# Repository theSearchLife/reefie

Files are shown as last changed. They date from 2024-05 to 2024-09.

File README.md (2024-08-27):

---
description: >-
  Data logging device for https://thesearch.life/the-coral-reef-philippines/
  project.
---

# Introduction

**Documentation view** - [https://thesearch-life.gitbook.io/reefie](https://thesearch-life.gitbook.io/reefie)

## Description

Battery powered device, encapsulated in watersealed enclosure to be able withstand 30m depths. It has sensory probes that capture and log data to SD card.

Data captured:

* Temperature
* Dissolved oxygen saturation
* Turbidity
* Conductivity
* Total dissolved solids
* Salinity
* Specific gravity
* Pressure

BOM -&#x20;

Hardware design done in FreeCAD 0.21.2 with Assembly4 workbench  for assembly. [https://github.com/theSearchLife/reefie/tree/main/hardware](https://github.com/theSearchLife/reefie/tree/main/hardware)

All files for 3D printing at [https://github.com/theSearchLife/reefie/tree/main/hardware/3D\_printing](https://github.com/theSearchLife/reefie/tree/main/hardware/3D\_printing) folder or can be exported from FreeCAD file.

Electronics wiring schematic in KiCAD 7.0 [https://github.com/theSearchLife/reefie/tree/main/hardware](https://github.com/theSearchLife/reefie/tree/main/hardware)

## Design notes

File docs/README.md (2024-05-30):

# Description

##

##

To pull CAD files install git LFS [https://git-lfs.com/](https://git-lfs.com/)

## BOM

### Custom cables

command for generating image from main dir

```
wireviz -f p -o docs/.gitbook/assets/ hardware/analog_harness.yaml
```

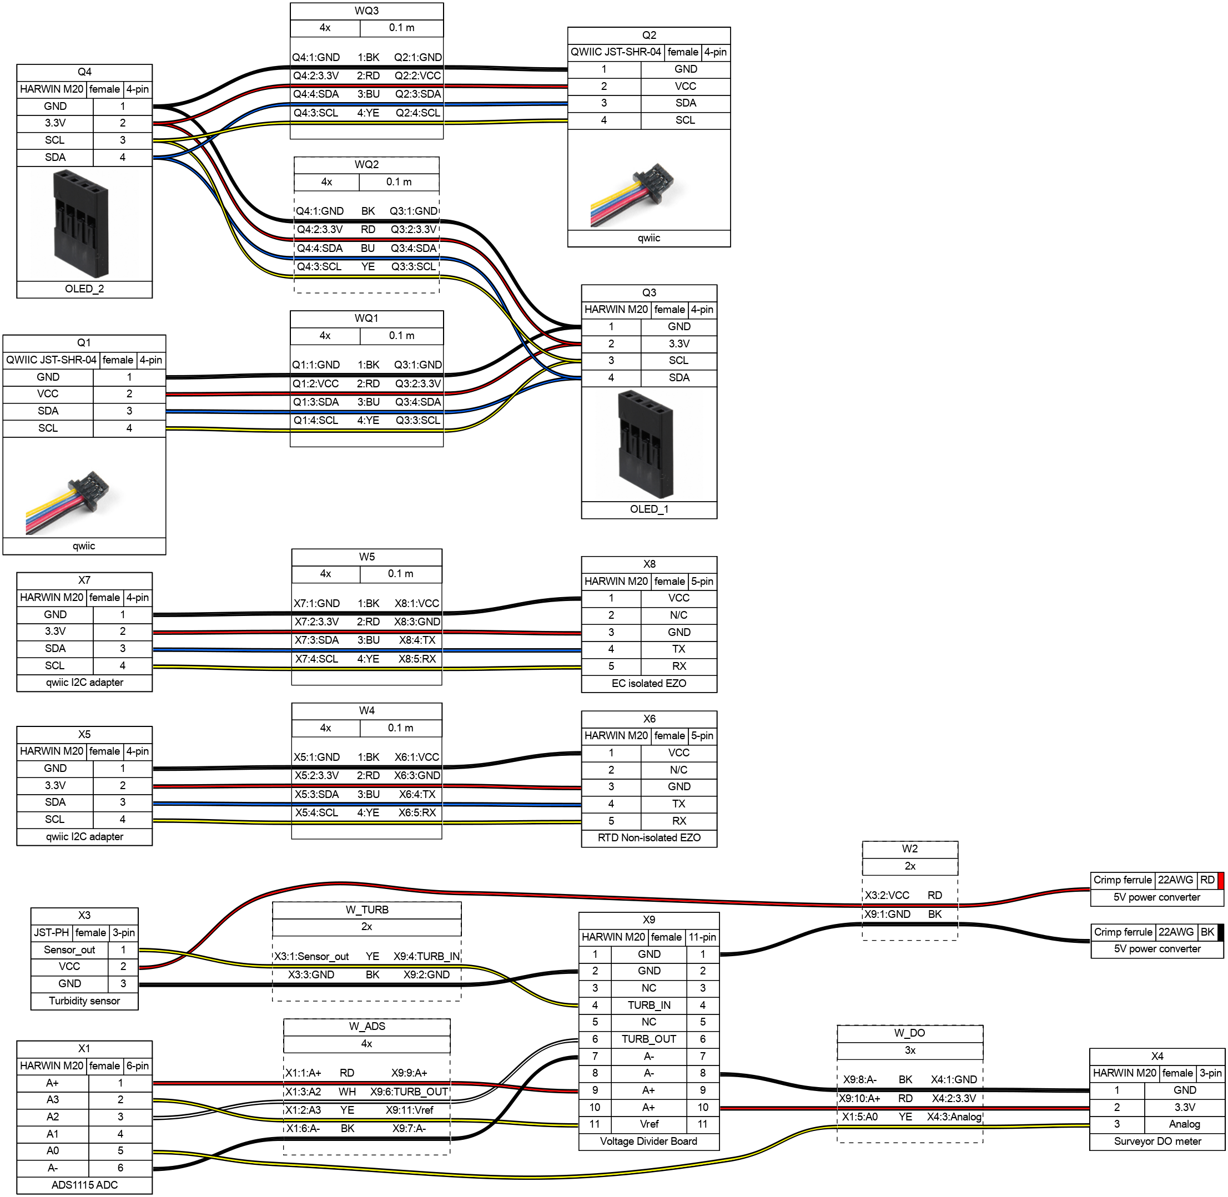
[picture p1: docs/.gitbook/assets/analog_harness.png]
<figure><figcaption></figcaption></figure>

## Firmware setup

VS Code

PlatformIO with dependencies

USB serial permissions

if USB device not found remove "apt remove brltty"

Depending on IDE need to manually configure to download mode\
\
Configure EZO probes to I2C mode

## Development notes

### I2C addresses

* 0x36 - MAX17048 - Fuel Gauge, Battery monitoring (on dev board)
* 0x48 - ADS1115 - ADC
* 0x49 - ADS1115 - (If A0/Addrees pin Soldered to HIGH) - ADC
* 0x64 - EZO-EC - Embedded Conductivity Circuit
* 0x66 - EZO-RTD Embedded Temperature Circuit
* 0x76 - MS5803-14BA - Pressure sensor

Can use Adafruit TestBed > I2CScan example to test/detect all I2C devices. [https://learn.adafruit.com/scanning-i2c-addresses/arduino-using-testbed](https://learn.adafruit.com/scanning-i2c-addresses/arduino-using-testbed)

## Useful links / References

<details>

<summary>SparkFun Thing Plus - ESP32 WROOM (USB-C)</summary>

* Sparkfun [https://www.sparkfun.com/products/20168](https://www.sparkfun.com/products/20168)
* Schematic [https://cdn.sparkfun.com/assets/5/9/7/4/1/SparkFun\_Thing\_Plus\_ESP32-WROOM\_C\_schematic2.pdf](https://cdn.sparkfun.com/assets/5/9/7/4/1/SparkFun\_Thing\_Plus\_ESP32-WROOM\_C\_schematic2.pdf)
* Graphical datasheet [https://cdn.sparkfun.com/assets/3/9/5/f/e/SparkFun\_Thing\_Plus\_ESP32\_WROOM\_C\_graphical\_datasheet2.pdf](https://cdn.sparkfun.com/assets/3/9/5/f/e/SparkFun\_Thing\_Plus\_ESP32\_WROOM\_C\_graphical\_datasheet2.pdf)
* GitHub Hardware repositore with firmware test for hardware features [https://github.com/sparkfun/SparkFun\_Thing\_Plus\_ESP32\_WROOM\_C](https://github.com/sparkfun/SparkFun\_Thing\_Plus\_ESP32\_WROOM\_C)

</details>

<details>

<summary>SparkFun Pressure Sensor Breakout - MS5803-14BA</summary>

* Sparkfun [https://www.sparkfun.com/products/12909](https://www.sparkfun.com/products/12909)
* Schematic - [https://cdn.sparkfun.com/datasheets/Sensors/Weather/MS5803-14BA\_Breakout\_v10.pdf](https://cdn.sparkfun.com/datasheets/Sensors/Weather/MS5803-14BA\_Breakout\_v10.pdf)
* Datasheet [https://cdn.sparkfun.com/datasheets/Sensors/Weather/ms5803\_14ba.pdf](https://cdn.sparkfun.com/datasheets/Sensors/Weather/ms5803\_14ba.pdf)

</details>

<details>

<summary>ADS115 Adafruit</summary>

* downloads [https://learn.adafruit.com/adafruit-4-channel-adc-breakouts/downloads](https://learn.adafruit.com/adafruit-4-channel-adc-breakouts/downloads)
* Pinouts [https://learn.adafruit.com/adafruit-4-channel-adc-breakouts/pinouts](https://learn.adafruit.com/adafruit-4-channel-adc-breakouts/pinouts)

</details>

<details>

<summary>Gravity: Analog Turbidity Sensor for Arduino</summary>

* DFRobot [https://www.dfrobot.com/product-1394.html](https://www.dfrobot.com/product-1394.html)
* DFRobot wiki [https://wiki.dfrobot.com/Turbidity\_sensor\_SKU\_\_SEN0189](https://wiki.dfrobot.com/Turbidity\_sensor\_SKU\_\_SEN0189)
* Sensor [https://dfimg.dfrobot.com/nobody/wiki/8e585d98aafe2bab22be39c5b68165c5.pdf](https://dfimg.dfrobot.com/nobody/wiki/8e585d98aafe2bab22be39c5b68165c5.pdf)
* Schematic [https://github.com/Arduinolibrary/DFRobot\_Turbidity\_sensor/blob/master/SEN0189%20Turbidity%20sensor%28V1.0%29%20schematic.pdf](https://github.com/Arduinolibrary/DFRobot\_Turbidity\_sensor/blob/master/SEN0189%20Turbidity%20sensor\(V1.0\)%20schematic.pdf)
* Probe [https://raw.githubusercontent.com/Arduinolibrary/DFRobot\_Turbidity\_sensor/master/Probe\_Dimension.png](https://raw.githubusercontent.com/Arduinolibrary/DFRobot\_Turbidity\_sensor/master/Probe\_Dimension.png)
* Adapter [https://raw.githubusercontent.com/Arduinolibrary/DFRobot\_Turbidity\_sensor/master/Adapter\_Dimension.png](https://raw.githubusercontent.com/Arduinolibrary/DFRobot\_Turbidity\_sensor/master/Adapter\_Dimension.png)

</details>

<details>

<summary>Gravity: Analog TDS Sensor/ Meter for Arduino</summary>

* DFRobot [https://www.dfrobot.com/product-1662.html](https://www.dfrobot.com/product-1662.html)
* DFRobot wiki [https://wiki.dfrobot.com/Gravity\_\_Analog\_TDS\_Sensor\_\_\_Meter\_For\_Arduino\_SKU\_\_SEN0244](https://wiki.dfrobot.com/Gravity\_\_Analog\_TDS\_Sensor\_\_\_Meter\_For\_Arduino\_SKU\_\_SEN0244)
* Schematic [https://raw.githubusercontent.com/Arduinolibrary/Gravity\_Analog\_TDS\_Sensor\_For\_Arduino/master/Analog%20TDS%20Sensor(V1.0)%20Schematic.pdf](https://raw.githubusercontent.com/Arduinolibrary/Gravity\_Analog\_TDS\_Sensor\_For\_Arduino/master/Analog%20TDS%20Sensor\(V1.0\)%20Schematic.pdf)
* Adapter layout [https://raw.githubusercontent.com/Arduinolibrary/Gravity\_Analog\_TDS\_Sensor\_For\_Arduino/master/Analog%20TDS%20Sensor(V1.0)%20Layout.pdf](https://raw.githubusercontent.com/Arduinolibrary/Gravity\_Analog\_TDS\_Sensor\_For\_Arduino/master/Analog%20TDS%20Sensor\(V1.0\)%20Layout.pdf)
* GitHub library [https://github.com/DFRobot/GravityTDS](https://github.com/DFRobot/GravityTDS)

</details>

<details>

<summary>PowerBoost 500 Basic - 5V USB Boost @ 500mA from 1.8V+</summary>

* Adafruit [https://www.adafruit.com/product/1903](https://www.adafruit.com/product/1903)
* Schematic [https://cdn-learn.adafruit.com/assets/assets/000/017/017/original/adafruit\_products\_tps61090.png?1401312193](https://cdn-learn.adafruit.com/assets/assets/000/017/017/original/adafruit\_products\_tps61090.png?1401312193)
* Datasheet [https://cdn-shop.adafruit.com/datasheets/tps61090.pdf](https://cdn-shop.adafruit.com/datasheets/tps61090.pdf)

</details>

<details>

<summary>Inline PT-1000 Temperature Kit</summary>

* AtlasScientific [https://atlas-scientific.com/kits/inline-temperature-kit/](https://atlas-scientific.com/kits/inline-temperature-kit/)
* EZO™ RTD Circuit Datasheet [https://files.atlas-scientific.com/EZO\_RTD\_Datasheet.pdf](https://files.atlas-scientific.com/EZO\_RTD\_Datasheet.pdf)
* PT-1000 Temperature Probe Datasheet [https://files.atlas-scientific.com/PT-1000-probe.pdf](https://files.atlas-scientific.com/PT-1000-probe.pdf)
* EZO™ Carrier Board Specsheet [https://files.atlas-scientific.com/EZO-carrier-board-non-isolated.pdf](https://files.atlas-scientific.com/EZO-carrier-board-non-isolated.pdf)
* Github I2C library [https://github.com/Atlas-Scientific/Ezo\_I2c\_lib](https://github.com/Atlas-Scientific/Ezo\_I2c\_lib)
* I2C Sample code [https://files.atlas-scientific.com/Ardunio-I2C-RTD-sample-code.pdf](https://files.atlas-scientific.com/Ardunio-I2C-RTD-sample-code.pdf)

</details>

<details>

<summary>Mini Conductivity K 1.0 Kit</summary>

* AtlasScientific [https://atlas-scientific.com/kits/mini-conductivity-k-1-0-kit/](https://atlas-scientific.com/kits/mini-conductivity-k-1-0-kit/)
* EZO™ Conductivity Circuit Datasheet [https://files.atlas-scientific.com/EC\_EZO\_Datasheet.pdf](https://files.atlas-scientific.com/EC\_EZO\_Datasheet.pdf)
* Mini Conductivity Probe K 1.0 Datasheet [https://files.atlas-scientific.com/Mini\_EC\_K\_1.0\_probe.pdf](https://files.atlas-scientific.com/Mini\_EC\_K\_1.0\_probe.pdf)
* Electrically Isolated EZO™ Carrier Board Datasheet [https://files.atlas-scientific.com/electrically-isolated-ezo-carrier-board.pdf](https://files.atlas-scientific.com/electrically-isolated-ezo-carrier-board.pdf)
* EZO™ Conductivity Accuracy Graph [https://files.atlas-scientific.com/conductivity\_accuracy\_graph.pdf](https://files.atlas-scientific.com/conductivity\_accuracy\_graph.pdf)
* Wiring Diagram [https://files.atlas-scientific.com/ezo-ec-wiringdiagram.pdf](https://files.atlas-scientific.com/ezo-ec-wiringdiagram.pdf)
* How to properly cut your probe cable [https://files.atlas-scientific.com/how-to-properly-cut-probe-cables.pdf](https://files.atlas-scientific.com/how-to-properly-cut-probe-cables.pdf)
* I2C sample code [https://files.atlas-scientific.com/Ardunio-I2C-EC-sample-code.pdf](https://files.atlas-scientific.com/Ardunio-I2C-EC-sample-code.pdf)
* EZO I2C Library [https://github.com/Atlas-Scientific/Ezo\_I2c\_lib](https://github.com/Atlas-Scientific/Ezo\_I2c\_lib)
* I2C mode selection [https://www.instructables.com/UART-AND-I2C-MODE-SWITCHING-FOR-ATLAS-SCIENTIFIC-E/](https://www.instructables.com/UART-AND-I2C-MODE-SWITCHING-FOR-ATLAS-SCIENTIFIC-E/)

</details>

<details>

<summary>Surveyor™ Analog Dissolved Oxygen Kit</summary>

* AtlasScientific [https://atlas-scientific.com/kits/surveyor-analog-do-kit/](https://atlas-scientific.com/kits/surveyor-analog-do-kit/)
* Surveyor™ Analog D.O. Meter Datasheet [https://files.atlas-scientific.com/Surveyor-DO-datasheet.pdf](https://files.atlas-scientific.com/Surveyor-DO-datasheet.pdf)
* Mini Lab Grade Dissolved Oxygen Probe Datasheet [https://files.atlas-scientific.com/Mini\_DO\_probe.pdf](https://files.atlas-scientific.com/Mini\_DO\_probe.pdf)
* Dissolved Oxygen | Common Mistakes | Air Bubble [https://youtu.be/1I1Sk9pt47c](https://youtu.be/1I1Sk9pt47c)
* Dissolved Oxygen | Common Mistakes | Stagnant vs Moving Water [https://youtu.be/d9zkxkv55SE](https://youtu.be/d9zkxkv55SE)
* Dissolved Oxygen | Common Mistakes | Damaged Membrane [https://youtu.be/PiXnvrTnVjs](https://youtu.be/PiXnvrTnVjs)
* Dissolved Oxygen Calculator [https://atlas-scientific.com/dissolved-oxygen-calculator](https://atlas-scientific.com/dissolved-oxygen-calculator)
* Arduino Sample Code [https://files.atlas-scientific.com/surveyor-DO-ardunio-code.pdf](https://files.atlas-scientific.com/surveyor-DO-ardunio-code.pdf)

</details>

<details>

<summary>Surveyor™ Analog pH Kit</summary>

* AtlastScientific [https://atlas-scientific.com/kits/surveyor-analog-ph-kit/](https://atlas-scientific.com/kits/surveyor-analog-ph-kit/)
* Surveyor™ Analog pH Sensor / Meter Datasheet [https://files.atlas-scientific.com/Surveyor-pH-datasheet.pdf](https://files.atlas-scientific.com/Surveyor-pH-datasheet.pdf)
* Consumer Grade pH Probe Datasheet [https://files.atlas-scientific.com/consumer-grade-pH-probe.pdf](https://files.atlas-scientific.com/consumer-grade-pH-probe.pdf)
* pH Temperature Compensation Calculator [https://atlas-scientific.com/ph-temperature-calculator/](https://atlas-scientific.com/ph-temperature-calculator/)
* Arduino Sample Code [https://files.atlas-scientific.com/surveyor-pH-ardunio-code.pdf](https://files.atlas-scientific.com/surveyor-pH-ardunio-code.pdf)
*

</details>

<details>

<summary>Surveyor™ Analog Isolator</summary>

* AtlasScientific [https://atlas-scientific.com/carrier-boards/surveyor-analog-isolator/](https://atlas-scientific.com/carrier-boards/surveyor-analog-isolator/)
* Surveyor™ Analog Isolator Datasheet [https://files.atlas-scientific.com/Surveyor\_analog\_isolator\_datasheet.pdf](https://files.atlas-scientific.com/Surveyor\_analog\_isolator\_datasheet.pdf)
* Arduino Sample Code [https://files.atlas-scientific.com/atlas\_surveyor.zip](https://files.atlas-scientific.com/atlas\_surveyor.zip)
* Surveyor™ Analog Isolator 3D model (\*step) [https://files.atlas-scientific.com/ISO-Gravity.zip](https://files.atlas-scientific.com/ISO-Gravity.zip)

</details>

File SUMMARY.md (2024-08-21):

# Table of contents

* [Introduction](README.md)
* [Assembly instructions](assembly-instructions/README.md)
  * [Sensors](assembly-instructions/page-1.md)
  * [Hardware](assembly-instructions/page-1-1.md)
  * [Electronics wiring](assembly-instructions/page-1-2.md)
  * [Inside Electronics](assembly-instructions/page-1-3.md)
  * [External assembly](assembly-instructions/external-assembly.md)
  * [Firmware setup](assembly-instructions/firmware-setup.md)
* [Usage / Maintenance](usage-maintenance.md)
* [Useful links / Datasheets / References](useful-links-datasheets-references.md)

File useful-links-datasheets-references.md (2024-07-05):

# Useful links / Datasheets / References

<details>

<summary>SparkFun Thing Plus - ESP32 WROOM (USB-C)</summary>

* Sparkfun [https://www.sparkfun.com/products/20168](https://www.sparkfun.com/products/20168)
* Schematic [https://cdn.sparkfun.com/assets/5/9/7/4/1/SparkFun\_Thing\_Plus\_ESP32-WROOM\_C\_schematic2.pdf](https://cdn.sparkfun.com/assets/5/9/7/4/1/SparkFun\_Thing\_Plus\_ESP32-WROOM\_C\_schematic2.pdf)
* Graphical datasheet [https://cdn.sparkfun.com/assets/3/9/5/f/e/SparkFun\_Thing\_Plus\_ESP32\_WROOM\_C\_graphical\_datasheet2.pdf](https://cdn.sparkfun.com/assets/3/9/5/f/e/SparkFun\_Thing\_Plus\_ESP32\_WROOM\_C\_graphical\_datasheet2.pdf)
* GitHub Hardware repositore with firmware test for hardware features [https://github.com/sparkfun/SparkFun\_Thing\_Plus\_ESP32\_WROOM\_C](https://github.com/sparkfun/SparkFun\_Thing\_Plus\_ESP32\_WROOM\_C)
* Fuel Gauge MAX17048 [https://cdn.sparkfun.com/assets/b/b/2/c/b/MAX17048.pdf](https://cdn.sparkfun.com/assets/b/b/2/c/b/MAX17048.pdf)

</details>

<details>

<summary>SparkFun Pressure Sensor Breakout - MS5803-14BA</summary>

* Sparkfun [https://www.sparkfun.com/products/12909](https://www.sparkfun.com/products/12909)
* Schematic - [https://cdn.sparkfun.com/datasheets/Sensors/Weather/MS5803-14BA\_Breakout\_v10.pdf](https://cdn.sparkfun.com/datasheets/Sensors/Weather/MS5803-14BA\_Breakout\_v10.pdf)
* Datasheet [https://cdn.sparkfun.com/datasheets/Sensors/Weather/ms5803\_14ba.pdf](https://cdn.sparkfun.com/datasheets/Sensors/Weather/ms5803\_14ba.pdf)

</details>

<details>

<summary>ADS115 Adafruit</summary>

* downloads [https://learn.adafruit.com/adafruit-4-channel-adc-breakouts/downloads](https://learn.adafruit.com/adafruit-4-channel-adc-breakouts/downloads)
* Pinouts [https://learn.adafruit.com/adafruit-4-channel-adc-breakouts/pinouts](https://learn.adafruit.com/adafruit-4-channel-adc-breakouts/pinouts)

</details>

<details>

<summary>RTC DS3231 Adafruit</summary>

* Adafruit [https://www.adafruit.com/product/5188](https://www.adafruit.com/product/5188)
* Adafruit Learning [https://learn.adafruit.com/adafruit-ds3231-precision-rtc-breakout/](https://learn.adafruit.com/adafruit-ds3231-precision-rtc-breakout/)
* Datasheet [https://www.analog.com/media/en/technical-documentation/data-sheets/DS3231.pdf](https://www.analog.com/media/en/technical-documentation/data-sheets/DS3231.pdf)
* Digikey [https://www.digikey.it/it/products/detail/adafruit-industries-llc/5188/15189155](https://www.digikey.it/it/products/detail/adafruit-industries-llc/5188/15189155)

</details>

<details>

<summary>Gravity: Analog Turbidity Sensor for Arduino</summary>

* DFRobot [https://www.dfrobot.com/product-1394.html](https://www.dfrobot.com/product-1394.html)
* DFRobot wiki [https://wiki.dfrobot.com/Turbidity\_sensor\_SKU\_\_SEN0189](https://wiki.dfrobot.com/Turbidity\_sensor\_SKU\_\_SEN0189)
* Sensor [https://dfimg.dfrobot.com/nobody/wiki/8e585d98aafe2bab22be39c5b68165c5.pdf](https://dfimg.dfrobot.com/nobody/wiki/8e585d98aafe2bab22be39c5b68165c5.pdf)
* Schematic [https://github.com/Arduinolibrary/DFRobot\_Turbidity\_sensor/blob/master/SEN0189%20Turbidity%20sensor%28V1.0%29%20schematic.pdf](https://github.com/Arduinolibrary/DFRobot\_Turbidity\_sensor/blob/master/SEN0189%20Turbidity%20sensor\(V1.0\)%20schematic.pdf)
* Probe [https://raw.githubusercontent.com/Arduinolibrary/DFRobot\_Turbidity\_sensor/master/Probe\_Dimension.png](https://raw.githubusercontent.com/Arduinolibrary/DFRobot\_Turbidity\_sensor/master/Probe\_Dimension.png)
* Adapter [https://raw.githubusercontent.com/Arduinolibrary/DFRobot\_Turbidity\_sensor/master/Adapter\_Dimension.png](https://raw.githubusercontent.com/Arduinolibrary/DFRobot\_Turbidity\_sensor/master/Adapter\_Dimension.png)

</details>

<details>

<summary>Gravity: Analog TDS Sensor/ Meter for Arduino</summary>

* DFRobot [https://www.dfrobot.com/product-1662.html](https://www.dfrobot.com/product-1662.html)
* DFRobot wiki [https://wiki.dfrobot.com/Gravity\_\_Analog\_TDS\_Sensor\_\_\_Meter\_For\_Arduino\_SKU\_\_SEN0244](https://wiki.dfrobot.com/Gravity\_\_Analog\_TDS\_Sensor\_\_\_Meter\_For\_Arduino\_SKU\_\_SEN0244)
* Schematic [https://raw.githubusercontent.com/Arduinolibrary/Gravity\_Analog\_TDS\_Sensor\_For\_Arduino/master/Analog%20TDS%20Sensor(V1.0)%20Schematic.pdf](https://raw.githubusercontent.com/Arduinolibrary/Gravity\_Analog\_TDS\_Sensor\_For\_Arduino/master/Analog%20TDS%20Sensor\(V1.0\)%20Schematic.pdf)
* Adapter layout [https://raw.githubusercontent.com/Arduinolibrary/Gravity\_Analog\_TDS\_Sensor\_For\_Arduino/master/Analog%20TDS%20Sensor(V1.0)%20Layout.pdf](https://raw.githubusercontent.com/Arduinolibrary/Gravity\_Analog\_TDS\_Sensor\_For\_Arduino/master/Analog%20TDS%20Sensor\(V1.0\)%20Layout.pdf)
* GitHub library [https://github.com/DFRobot/GravityTDS](https://github.com/DFRobot/GravityTDS)

</details>

<details>

<summary>PowerBoost 500 Basic - 5V USB Boost @ 500mA from 1.8V+</summary>

* Adafruit [https://www.adafruit.com/product/1903](https://www.adafruit.com/product/1903)
* Schematic [https://cdn-learn.adafruit.com/assets/assets/000/017/017/original/adafruit\_products\_tps61090.png?1401312193](https://cdn-learn.adafruit.com/assets/assets/000/017/017/original/adafruit\_products\_tps61090.png?1401312193)
* Datasheet [https://cdn-shop.adafruit.com/datasheets/tps61090.pdf](https://cdn-shop.adafruit.com/datasheets/tps61090.pdf)

</details>

<details>

<summary>Inline PT-1000 Temperature Kit</summary>

* AtlasScientific [https://atlas-scientific.com/kits/inline-temperature-kit/](https://atlas-scientific.com/kits/inline-temperature-kit/)
* EZO™ RTD Circuit Datasheet [https://files.atlas-scientific.com/EZO\_RTD\_Datasheet.pdf](https://files.atlas-scientific.com/EZO\_RTD\_Datasheet.pdf)
* PT-1000 Temperature Probe Datasheet [https://files.atlas-scientific.com/PT-1000-probe.pdf](https://files.atlas-scientific.com/PT-1000-probe.pdf)
* EZO™ Carrier Board Specsheet [https://files.atlas-scientific.com/EZO-carrier-board-non-isolated.pdf](https://files.atlas-scientific.com/EZO-carrier-board-non-isolated.pdf)
* Github I2C library [https://github.com/Atlas-Scientific/Ezo\_I2c\_lib](https://github.com/Atlas-Scientific/Ezo\_I2c\_lib)
* I2C Sample code [https://files.atlas-scientific.com/Ardunio-I2C-RTD-sample-code.pdf](https://files.atlas-scientific.com/Ardunio-I2C-RTD-sample-code.pdf)

</details>

<details>

<summary>Mini Conductivity K 1.0 Kit</summary>

* AtlasScientific [https://atlas-scientific.com/kits/mini-conductivity-k-1-0-kit/](https://atlas-scientific.com/kits/mini-conductivity-k-1-0-kit/)
* EZO™ Conductivity Circuit Datasheet [https://files.atlas-scientific.com/EC\_EZO\_Datasheet.pdf](https://files.atlas-scientific.com/EC\_EZO\_Datasheet.pdf)
* Mini Conductivity Probe K 1.0 Datasheet [https://files.atlas-scientific.com/Mini\_EC\_K\_1.0\_probe.pdf](https://files.atlas-scientific.com/Mini\_EC\_K\_1.0\_probe.pdf)
* Electrically Isolated EZO™ Carrier Board Datasheet [https://files.atlas-scientific.com/electrically-isolated-ezo-carrier-board.pdf](https://files.atlas-scientific.com/electrically-isolated-ezo-carrier-board.pdf)
* EZO™ Conductivity Accuracy Graph [https://files.atlas-scientific.com/conductivity\_accuracy\_graph.pdf](https://files.atlas-scientific.com/conductivity\_accuracy\_graph.pdf)
* Wiring Diagram [https://files.atlas-scientific.com/ezo-ec-wiringdiagram.pdf](https://files.atlas-scientific.com/ezo-ec-wiringdiagram.pdf)
* How to properly cut your probe cable [https://files.atlas-scientific.com/how-to-properly-cut-probe-cables.pdf](https://files.atlas-scientific.com/how-to-properly-cut-probe-cables.pdf)
* I2C sample code [https://files.atlas-scientific.com/Ardunio-I2C-EC-sample-code.pdf](https://files.atlas-scientific.com/Ardunio-I2C-EC-sample-code.pdf)
* EZO I2C Library [https://github.com/Atlas-Scientific/Ezo\_I2c\_lib](https://github.com/Atlas-Scientific/Ezo\_I2c\_lib)
* I2C mode selection [https://www.instructables.com/UART-AND-I2C-MODE-SWITCHING-FOR-ATLAS-SCIENTIFIC-E/](https://www.instructables.com/UART-AND-I2C-MODE-SWITCHING-FOR-ATLAS-SCIENTIFIC-E/)

</details>

<details>

<summary>Surveyor™ Analog Dissolved Oxygen Kit</summary>

* AtlasScientific [https://atlas-scientific.com/kits/surveyor-analog-do-kit/](https://atlas-scientific.com/kits/surveyor-analog-do-kit/)
* Surveyor™ Analog D.O. Meter Datasheet [https://files.atlas-scientific.com/Surveyor-DO-datasheet.pdf](https://files.atlas-scientific.com/Surveyor-DO-datasheet.pdf)
* Mini Lab Grade Dissolved Oxygen Probe Datasheet [https://files.atlas-scientific.com/Mini\_DO\_probe.pdf](https://files.atlas-scientific.com/Mini\_DO\_probe.pdf)
* Dissolved Oxygen | Common Mistakes | Air Bubble [https://youtu.be/1I1Sk9pt47c](https://youtu.be/1I1Sk9pt47c)
* Dissolved Oxygen | Common Mistakes | Stagnant vs Moving Water [https://youtu.be/d9zkxkv55SE](https://youtu.be/d9zkxkv55SE)
* Dissolved Oxygen | Common Mistakes | Damaged Membrane [https://youtu.be/PiXnvrTnVjs](https://youtu.be/PiXnvrTnVjs)
* Dissolved Oxygen Calculator [https://atlas-scientific.com/dissolved-oxygen-calculator](https://atlas-scientific.com/dissolved-oxygen-calculator)
* Arduino Sample Code [https://files.atlas-scientific.com/surveyor-DO-ardunio-code.pdf](https://files.atlas-scientific.com/surveyor-DO-ardunio-code.pdf)

</details>

<details>

<summary>Surveyor™ Analog pH Kit</summary>

* AtlastScientific [https://atlas-scientific.com/kits/surveyor-analog-ph-kit/](https://atlas-scientific.com/kits/surveyor-analog-ph-kit/)
* Surveyor™ Analog pH Sensor / Meter Datasheet [https://files.atlas-scientific.com/Surveyor-pH-datasheet.pdf](https://files.atlas-scientific.com/Surveyor-pH-datasheet.pdf)
* Consumer Grade pH Probe Datasheet [https://files.atlas-scientific.com/consumer-grade-pH-probe.pdf](https://files.atlas-scientific.com/consumer-grade-pH-probe.pdf)
* pH Temperature Compensation Calculator [https://atlas-scientific.com/ph-temperature-calculator/](https://atlas-scientific.com/ph-temperature-calculator/)
* Arduino Sample Code [https://files.atlas-scientific.com/surveyor-pH-ardunio-code.pdf](https://files.atlas-scientific.com/surveyor-pH-ardunio-code.pdf)
*

</details>

<details>

<summary>Surveyor™ Analog Isolator</summary>

* AtlasScientific [https://atlas-scientific.com/carrier-boards/surveyor-analog-isolator/](https://atlas-scientific.com/carrier-boards/surveyor-analog-isolator/)
* Surveyor™ Analog Isolator Datasheet [https://files.atlas-scientific.com/Surveyor\_analog\_isolator\_datasheet.pdf](https://files.atlas-scientific.com/Surveyor\_analog\_isolator\_datasheet.pdf)
* Arduino Sample Code [https://files.atlas-scientific.com/atlas\_surveyor.zip](https://files.atlas-scientific.com/atlas\_surveyor.zip)
* Surveyor™ Analog Isolator 3D model (\*step) [https://files.atlas-scientific.com/ISO-Gravity.zip](https://files.atlas-scientific.com/ISO-Gravity.zip)

</details>

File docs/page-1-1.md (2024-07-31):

---
description: Preparation of sensors
---

# Sensors

## Pressure

<details>

<summary>MS583730BA01-50</summary>

**Components**

* Sensor [https://www.digikey.it/en/products/detail/te-connectivity-measurement-specialties/MS583730BA01-50/5629501?s=N4IgTCBcDaILIGUCsAOAzAdjQBgEIEFsBGAWiWxAF0BfIA](https://www.digikey.it/en/products/detail/te-connectivity-measurement-specialties/MS583730BA01-50/5629501?s=N4IgTCBcDaILIGUCsAOAzAdjQBgEIEFsBGAWiWxAF0BfIA)
* 3D printed
  * MS583730BA01-50-Enclosure\_inner
  * MS583730BA01-50- Enclosure\_outer
* Cable&#x20;
* SMD 0.1uF Capacitor
* o-ring
* Flexible Urethane 8800
  * Syringe to inject liquid inside casing

**Steps**

*   3D print

    * 6 Layer walls
    * 100% infill
    * PETG

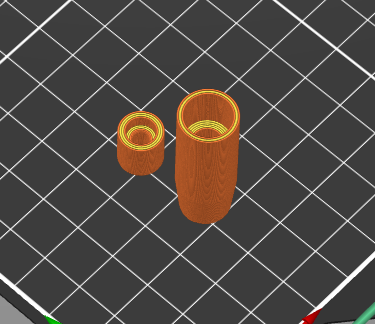
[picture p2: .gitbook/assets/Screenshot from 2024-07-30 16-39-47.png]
    

<!---->

* Solder capacitor and cable

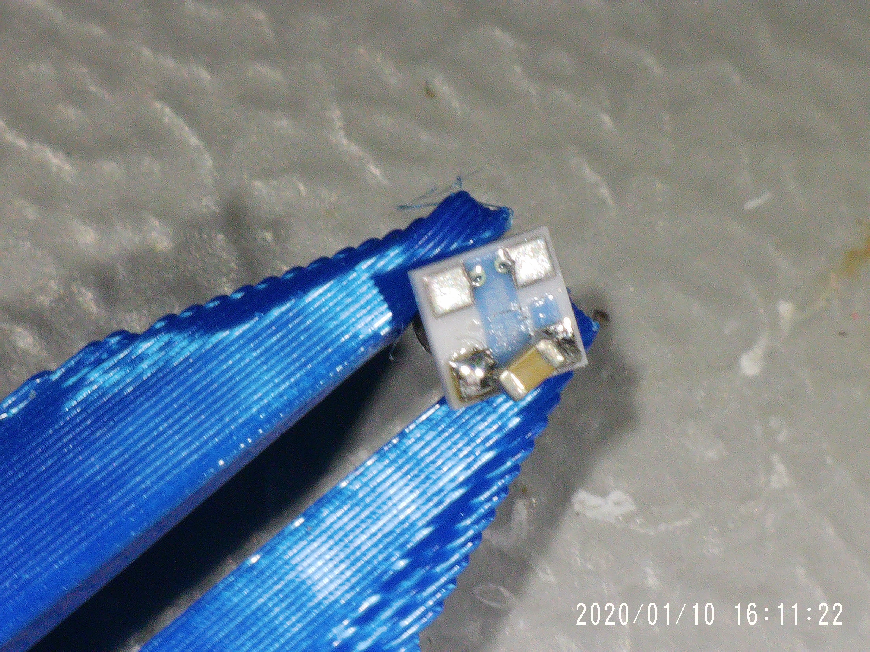
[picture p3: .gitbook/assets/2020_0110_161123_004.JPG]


* Apply conformal coating on soldering
* Install o-ring to sensor
* Clean cable with IPA
* Insert sensor to casing

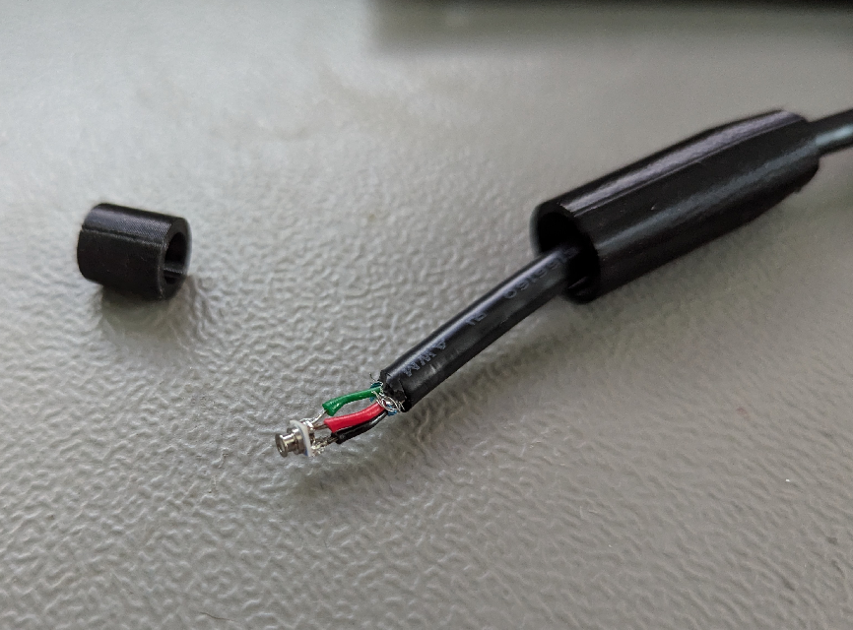
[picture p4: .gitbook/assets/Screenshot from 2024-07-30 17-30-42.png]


* Mount external casing

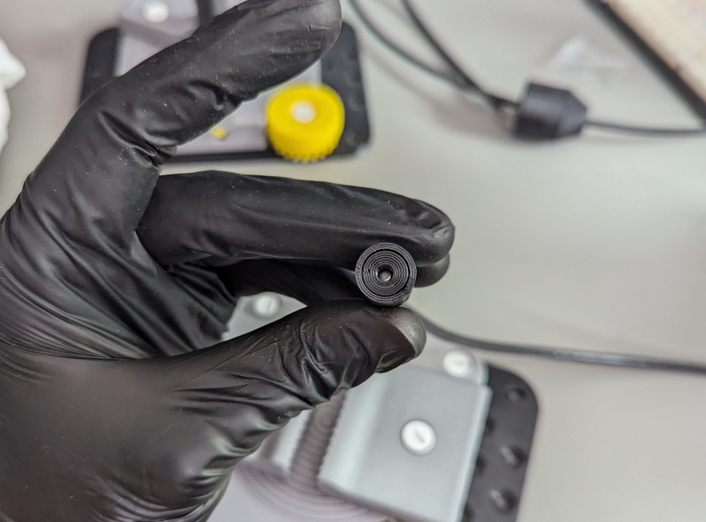
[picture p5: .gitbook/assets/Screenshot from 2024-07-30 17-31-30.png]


* Apply tape on the end to prevent leaking

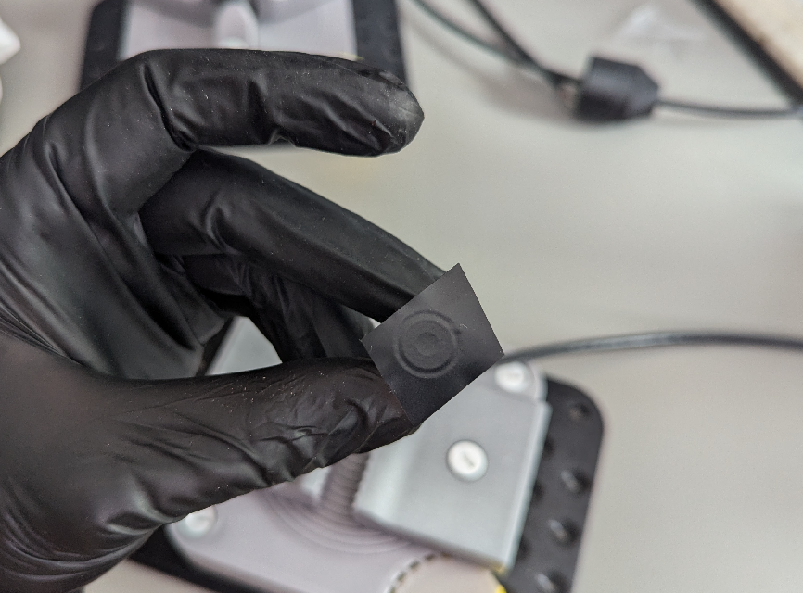
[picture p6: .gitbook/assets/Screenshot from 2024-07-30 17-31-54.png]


* Fill casing with Urethane (using syringe)

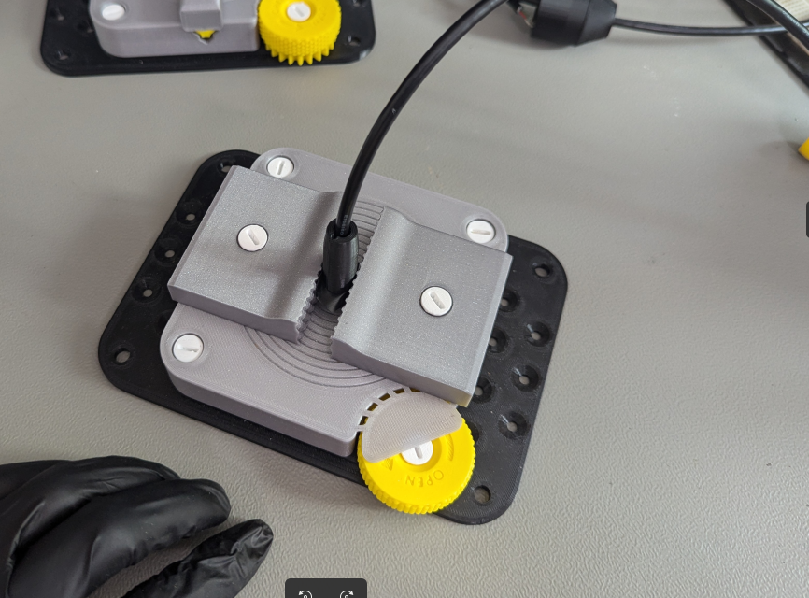
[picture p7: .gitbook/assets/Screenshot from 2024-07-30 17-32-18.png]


* Cure it

</details>

<details>

<summary>MS580314BA01-00</summary>

**Components**

* Sensor
* 3D printed
  * MS580314BA01-00-Enclosure\_inner
  * MS580314BA01-00 - Enclosure\_outer
* Cable
* Flexible Urethane 8800

**Steps**

* 3D print
  * 6 Layer walls
  * 100% infill
  * PETG

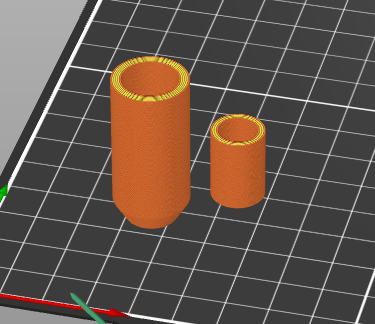
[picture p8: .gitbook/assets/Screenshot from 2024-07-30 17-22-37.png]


* Solder capacitor and cable
* Apply conformal coating
* Clean cable with IPA
* Insert sensor to casing

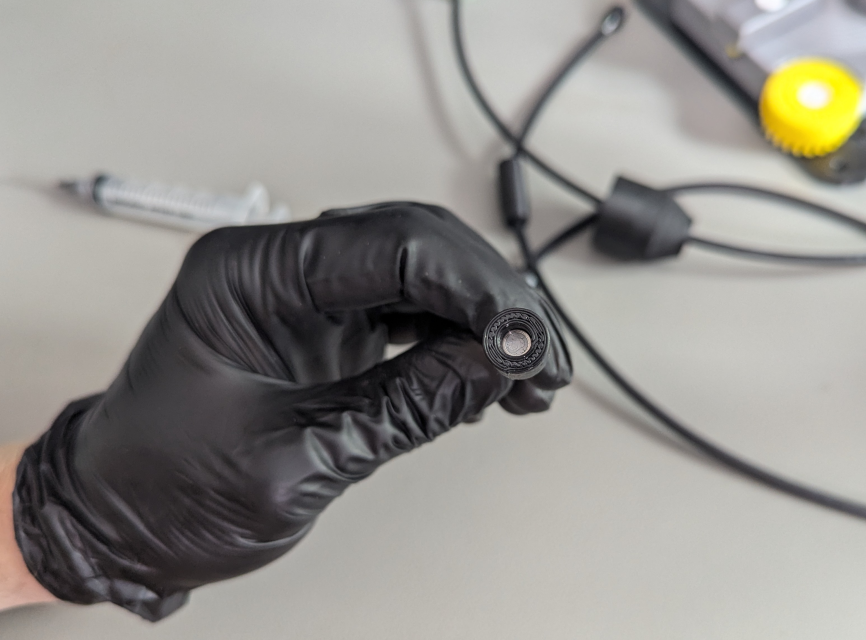
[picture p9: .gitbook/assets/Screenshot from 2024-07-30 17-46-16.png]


* Mount external casing
* Apply tape to prevent Urethane leaking

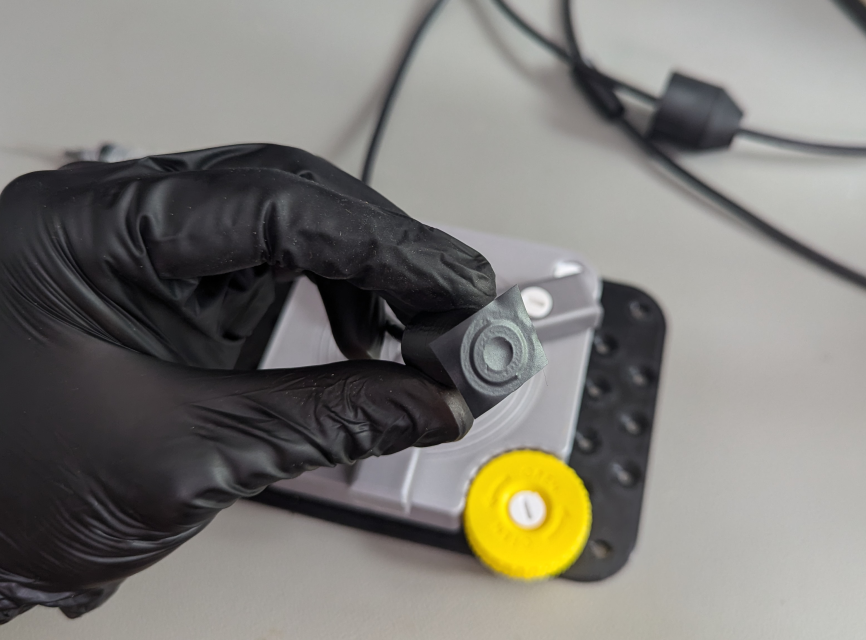
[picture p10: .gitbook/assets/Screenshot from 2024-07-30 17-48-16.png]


* Fill casing with Urethane
* Cure itdone

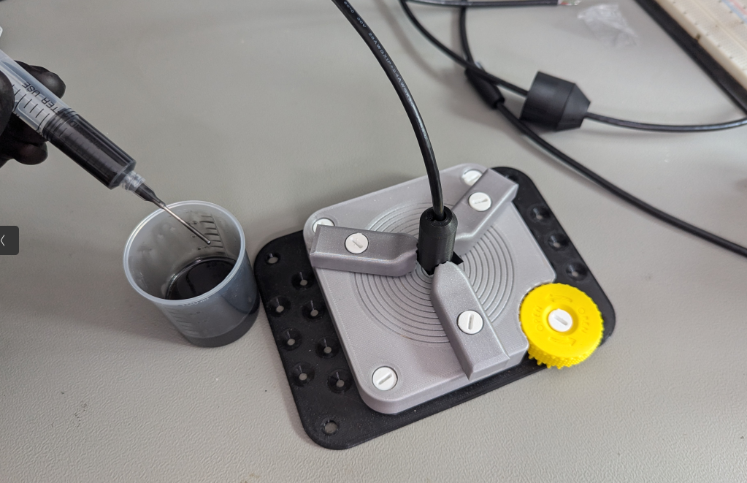
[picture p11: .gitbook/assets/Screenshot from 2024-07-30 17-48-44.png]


</details>

## Turbidity sensor

* Sensor [https://www.dfrobot.com/product-1394.html](https://www.dfrobot.com/product-1394.html)
* 3D print Casing
  * Turbidity\_Cover
  * 6 Layer wall
  * 100% infill
  * 10mm Brim width
  * PETG

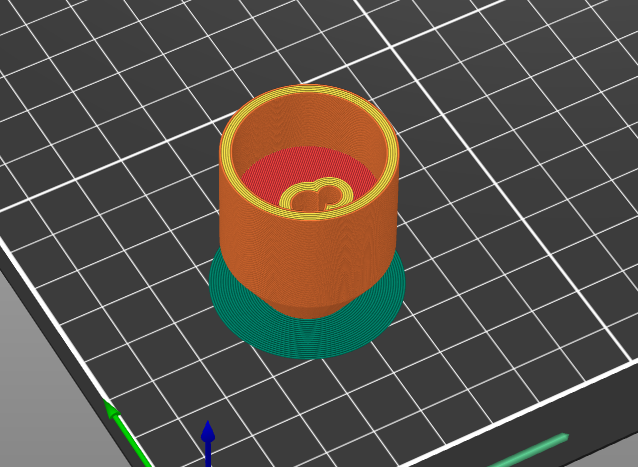
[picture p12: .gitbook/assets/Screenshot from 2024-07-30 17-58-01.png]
<figure><figcaption></figcaption></figure>

* Desolder JST connector

<div>

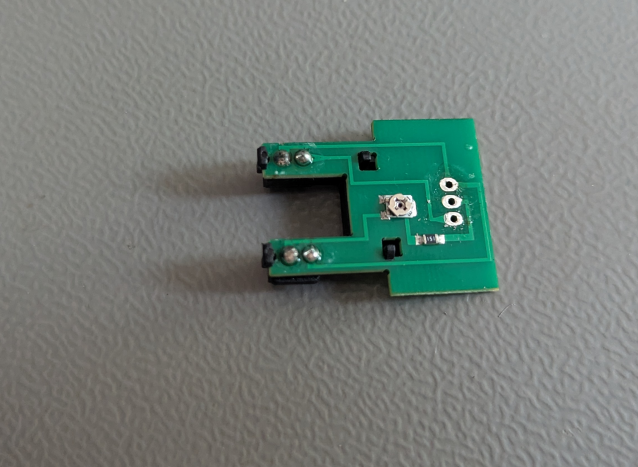
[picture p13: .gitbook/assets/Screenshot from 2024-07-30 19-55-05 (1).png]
<figure><figcaption></figcaption></figure>

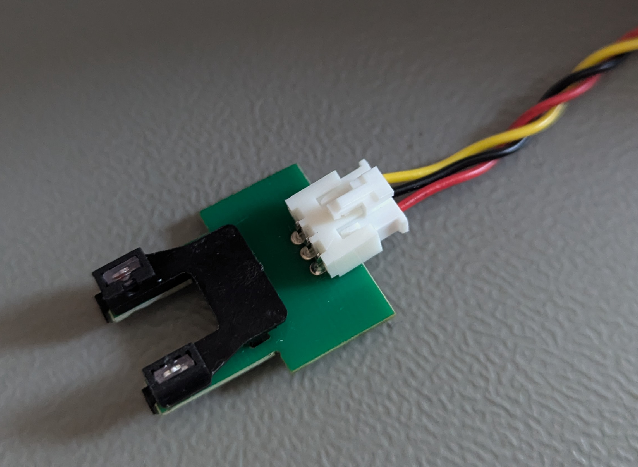
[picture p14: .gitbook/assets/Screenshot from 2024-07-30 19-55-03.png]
<figure><figcaption></figcaption></figure>

</div>

* Solder the cable
  * Red - VCC
  * Black - GND
  * Green - Signal

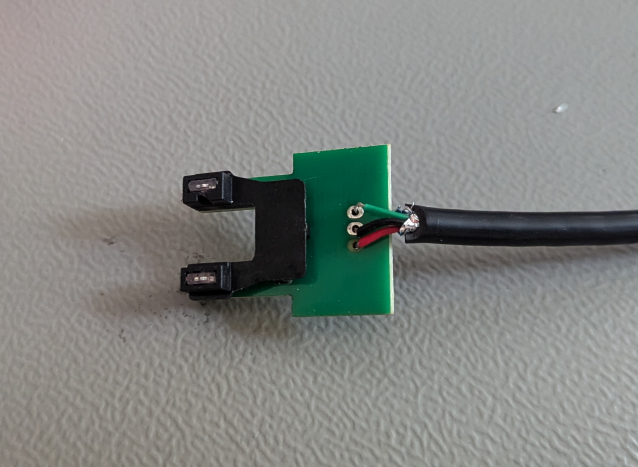
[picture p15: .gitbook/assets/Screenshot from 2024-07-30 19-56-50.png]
<figure><figcaption></figcaption></figure>

* Hot Glue the wires to keep them in place
* Fill hot glue around sensor are to seal it, preventing Urethane filling sensor are

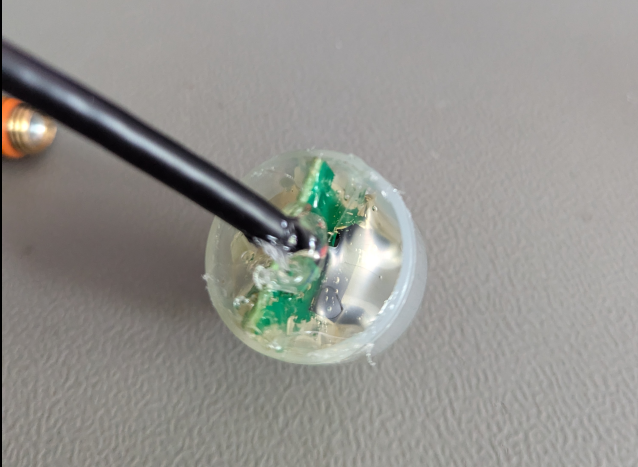
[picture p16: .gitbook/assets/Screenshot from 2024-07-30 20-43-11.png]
<figure><figcaption></figcaption></figure>

* Install casing
* Fill with Urethane

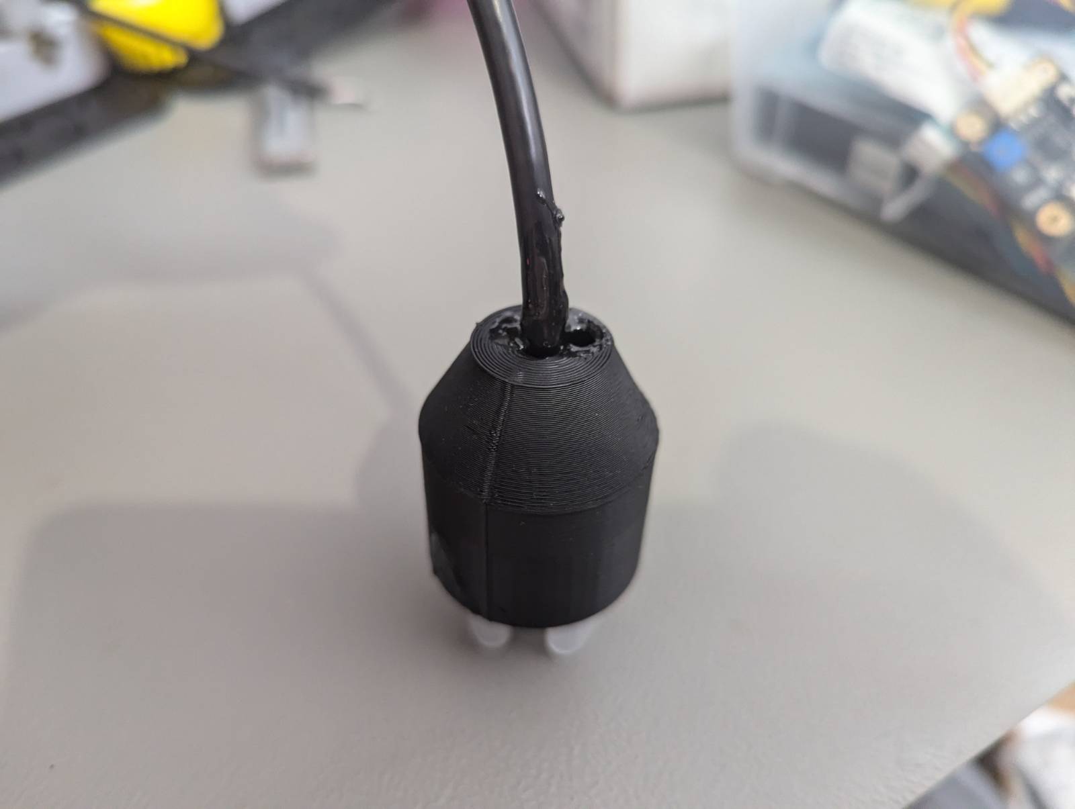
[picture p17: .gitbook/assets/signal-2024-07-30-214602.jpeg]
<figure><figcaption></figcaption></figure>

## Temperature

### PCB assembly

### EZOboard I2C mode selection

### Calibration

## Dissolved Oxygen

## Conductivity

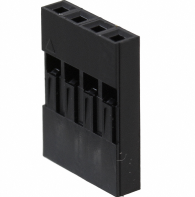
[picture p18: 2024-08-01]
hardware/resources/HARWIN_M20_4.png

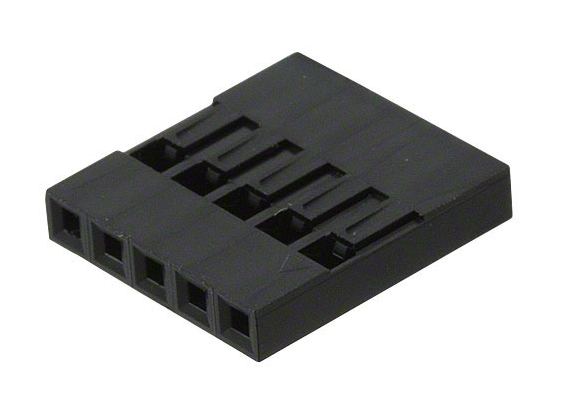
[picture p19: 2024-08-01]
hardware/resources/HARWIN_M20_5.png

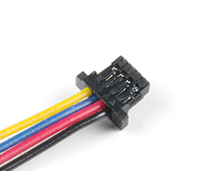
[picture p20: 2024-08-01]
hardware/resources/qwiic_cable.png

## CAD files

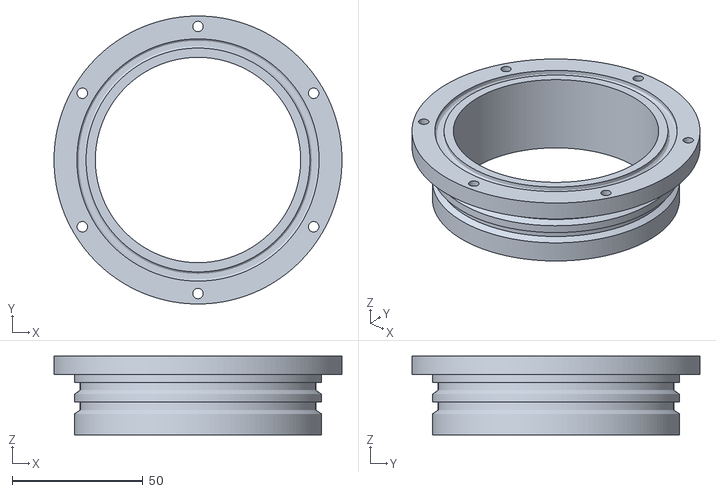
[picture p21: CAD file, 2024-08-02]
hardware/3D_printing/flange/Master-FlangeSeal_Open (Meshed).stl
110.0 x 110.0 x 30.1

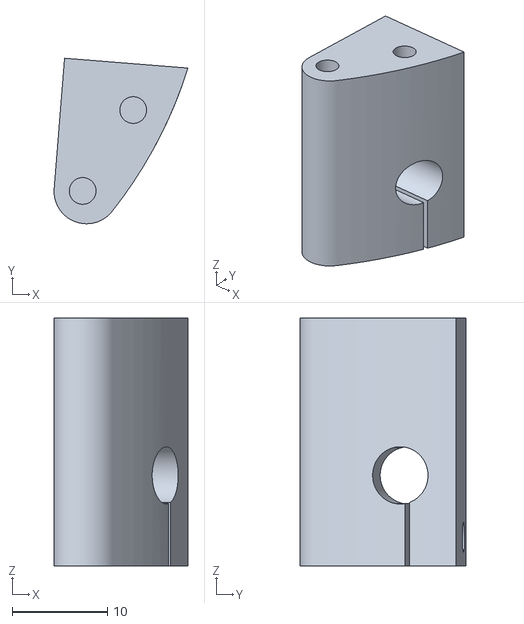
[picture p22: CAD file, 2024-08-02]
hardware/3D_printing/Inside/Master-ReedSwitchHolder_v2 (Meshed).stl
14.0 x 17.4 x 26.0

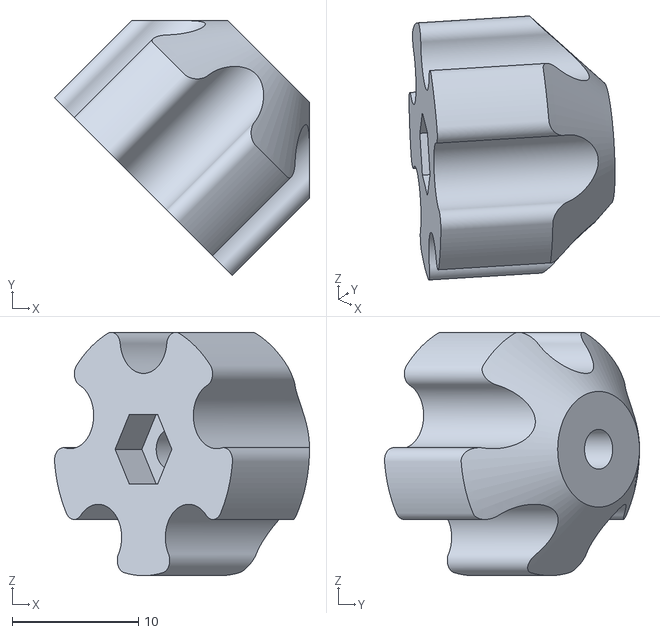
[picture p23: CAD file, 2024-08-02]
hardware/3D_printing/outside/Master-Knob (Meshed).stl
20.2 x 20.2 x 19.2

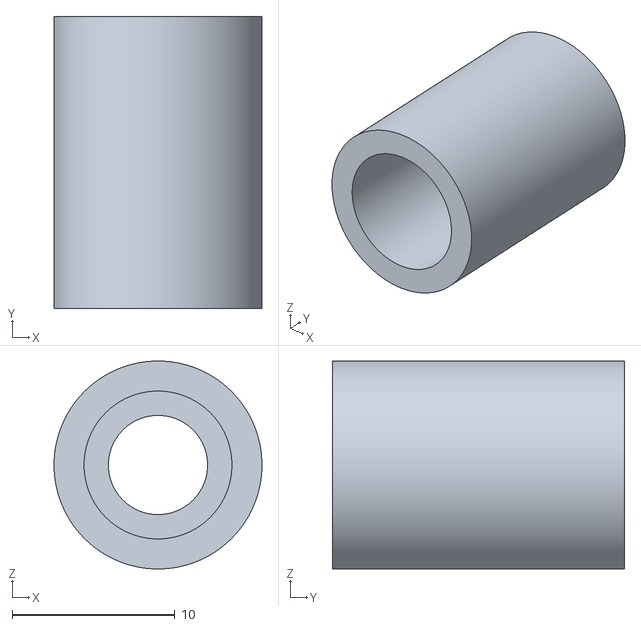
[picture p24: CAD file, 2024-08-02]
hardware/3D_printing/sensors/Master-MS580314BA01-00-Enclosure_inner (Meshed).stl
12.8 x 18.0 x 12.8

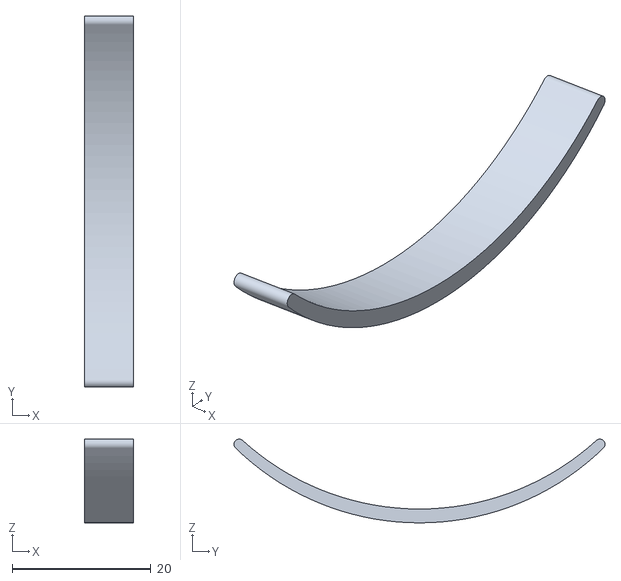
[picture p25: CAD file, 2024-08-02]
hardware/3D_printing/switch/Master-SwitchSpring (Meshed).stl
7.00 x 53.5 x 12.1

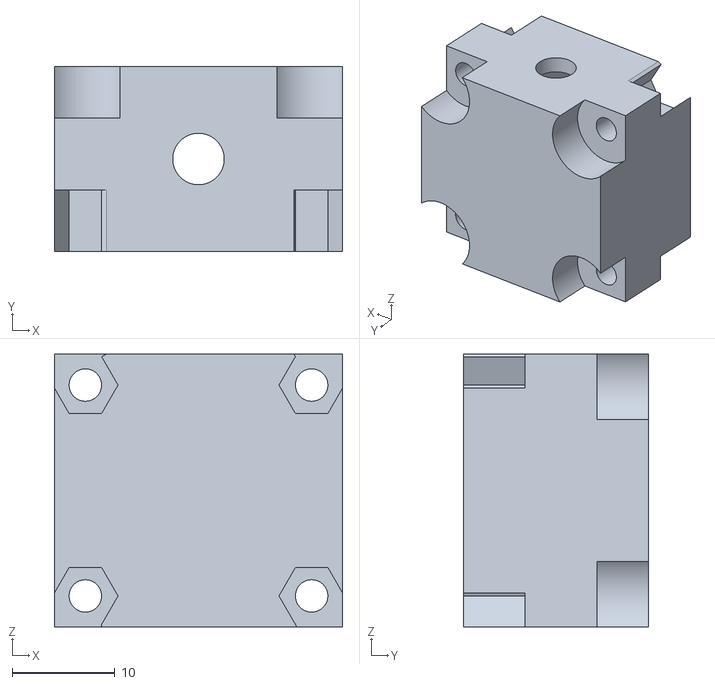
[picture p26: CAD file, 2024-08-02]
hardware/3D_printing/tools/Master-CustomSealMould001 (Meshed).stl
28.0 x 18.0 x 26.5

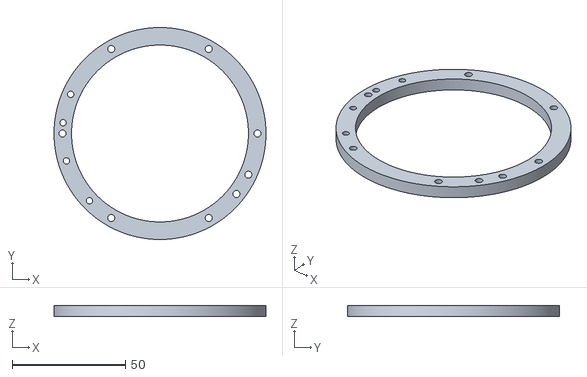
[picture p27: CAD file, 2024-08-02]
hardware/3D_printing/Inside/Master-ConnectingRing_top (Meshed).stl
93.5 x 93.5 x 5.00

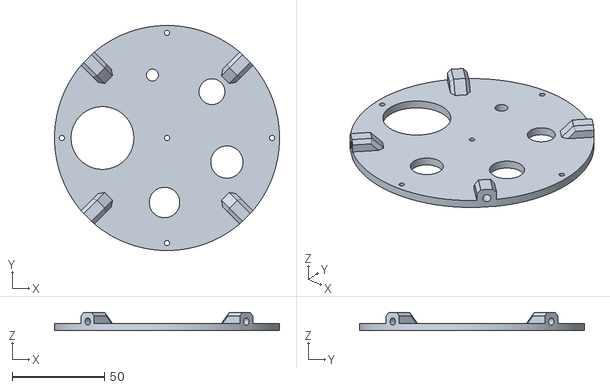
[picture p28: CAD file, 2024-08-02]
hardware/3D_printing/outside/Master-SensorMountingPlate (Meshed).stl
122.0 x 122.0 x 10.0

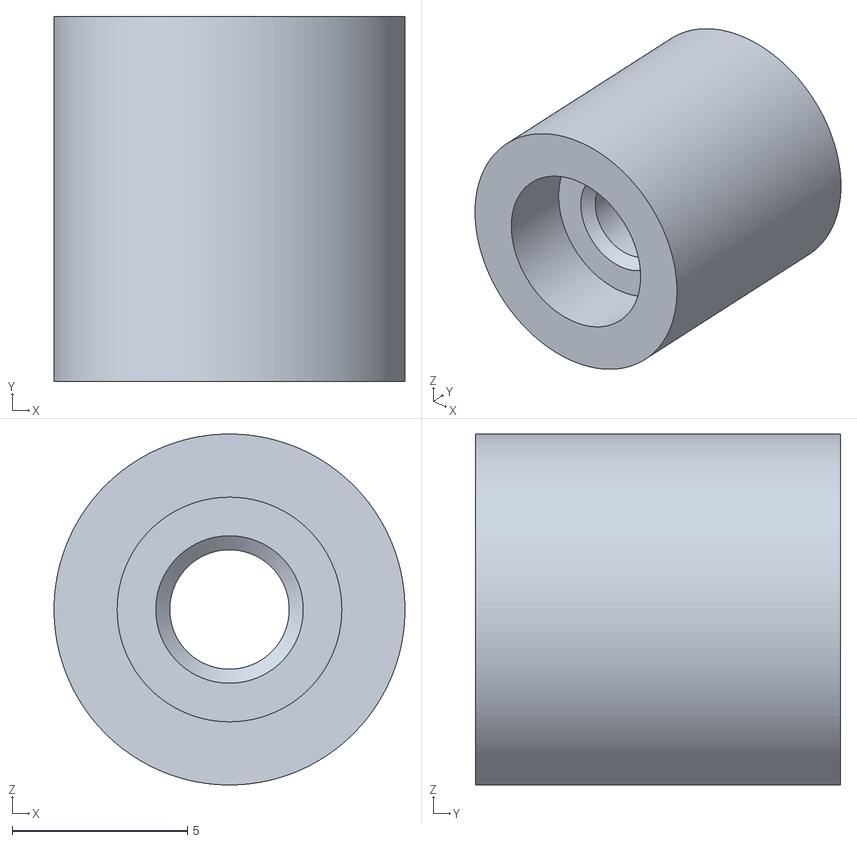
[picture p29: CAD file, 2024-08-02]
hardware/3D_printing/sensors/Master-MS583730BA01-50-Enclosure_inner (Meshed).stl
10.0 x 10.4 x 10.0

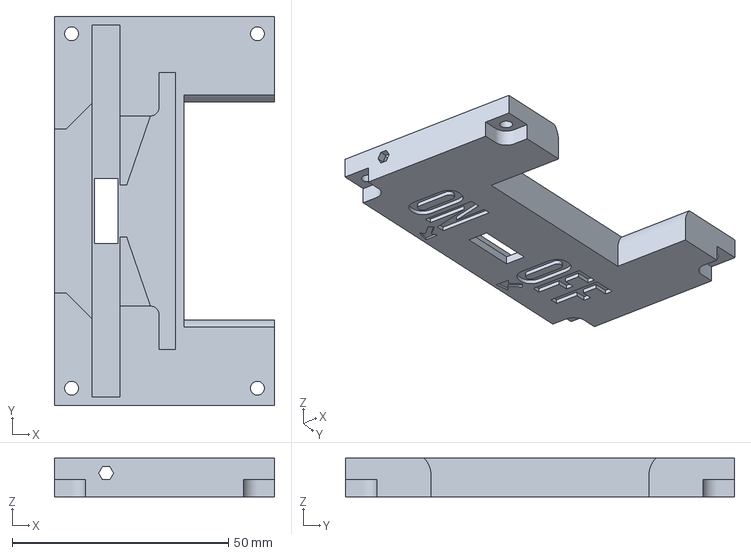
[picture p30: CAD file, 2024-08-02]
hardware/3D_printing/switch/Master-SwitchLid_withText (Meshed).3mf
51.0 x 90.0 x 9.00 mm

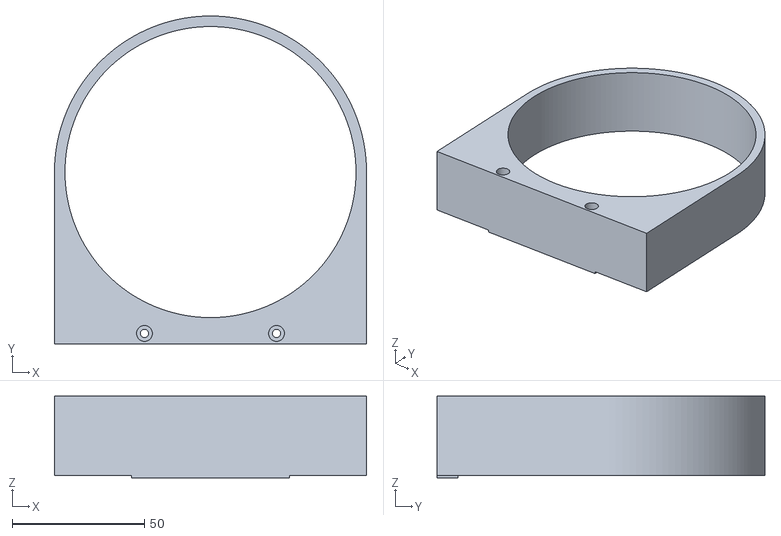
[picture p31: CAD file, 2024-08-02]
hardware/3D_printing/tools/Master-TubCuttingGuide001 (Meshed).stl
118.2 x 124.2 x 31.0

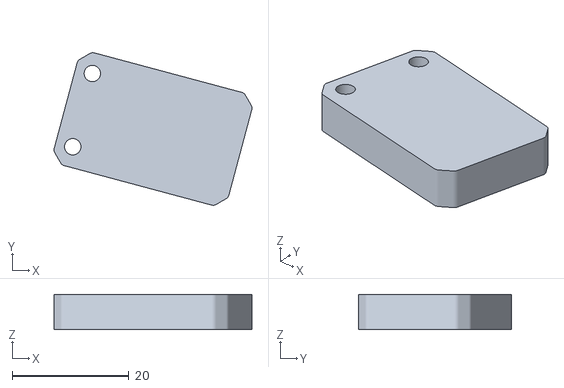
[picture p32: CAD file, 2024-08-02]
hardware/3D_printing/Inside/Master-VD_holder (Meshed).stl
33.9 x 26.2 x 6.00

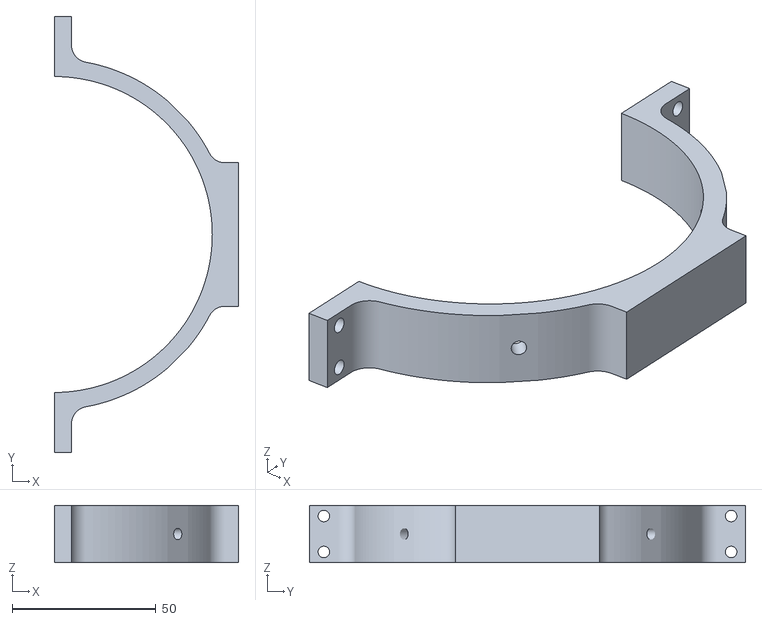
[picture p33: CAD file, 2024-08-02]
hardware/3D_printing/outside/Master-Clamp_bottom003.stl
64.2 x 151.8 x 20.0

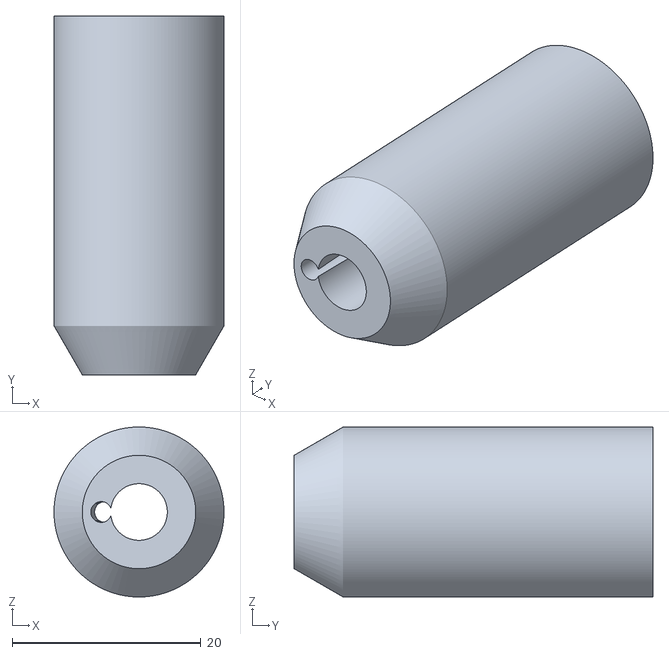
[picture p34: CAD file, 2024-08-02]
hardware/3D_printing/sensors/Master-MS580314BA01-00 - Enclosure_outer (Meshed).stl
18.0 x 38.0 x 18.0

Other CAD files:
hardware/3D_printing/switch/Master-SwitchSlider_withText (Meshed).stl
hardware/3D_printing/tools/Master-TubCuttingGuide002 (Meshed).stl
hardware/3D_printing/Inside/Master-CableGland_cableclamp (Meshed).stl
hardware/3D_printing/outside/Master-SensorCover (Meshed).stl
hardware/3D_printing/Inside/Master-BatteryHolder_v004 (Meshed).stl
hardware/3D_printing/Inside/Master-ConnectingRing_bottom (Meshed).stl
hardware/3D_printing/Inside/Master-Display_holder_1.3_ (Meshed).stl
hardware/3D_printing/Inside/Master-SensorStackAttachment (Meshed).stl
hardware/3D_printing/Inside/Master-o-ring-protection (Meshed).stl
hardware/3D_printing/outside/Master-Clamp_top (Meshed).stl
hardware/3D_printing/outside/Master-Handle_curved (Meshed).stl
hardware/3D_printing/sensors/Master-MS580314BA01-00 - Enclosure (Meshed).stl
hardware/3D_printing/sensors/Master-MS580314BA01-00-Enclosure002 (Meshed).stl
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

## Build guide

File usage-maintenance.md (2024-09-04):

# Usage / Maintenance

## Data description

* **unix\_timestamp** - It shows the time in Unix format, representing the number of seconds that have elapsed since January 1, 1970 (UTC). This value is used for precise time-stamping of sensor data.
*   **human\_timestamp** - It shows the time in a human-readable format (e.g., YYYY-MM-DD HH:MM

    ), making it easier to understand the exact date and time when the data was recorded.
* **temperature** - It shows the water temperature in degrees Celsius (°C), an important factor that affects dissolved oxygen levels, conductivity, and other water quality parameters.
* **do\_volt** - It shows the voltage output from the dissolved oxygen (DO) sensor. This raw voltage value is used to calculate the concentration or saturation level of dissolved oxygen in the water.
* **do\_saturation** - It shows the percentage of oxygen saturation in the water. This value indicates the amount of dissolved oxygen relative to the maximum amount that water can hold at a specific temperature and pressure.
* **turb\_volt** - It shows the voltage output from the turbidity sensor. This raw voltage value is used to determine the turbidity of the water, which indicates how clear or murky it is.
* **turb\_ntu** - It shows the turbidity of the water in Nephelometric Turbidity Units (NTU). This value indicates the concentration of suspended particles in the water, which can affect light penetration and aquatic life. (Calibration is not accurate, use only for relative values)
* **conductivity** - It shows the electrical conductivity of the water in microsiemens per centimeter (µS/cm). This value indicates the water's ability to conduct electricity, which is influenced by the presence of dissolved salts and minerals.
* **tds** - It shows the total dissolved solids (TDS) in the water, typically measured in milligrams per liter (mg/L). This value represents the combined content of all inorganic and organic substances dissolved in the water.
* **salinity** - It shows the concentration of salt in the water, typically measured in parts per thousand (ppt) or practical salinity units (PSU). This value is important for understanding the water's chemical properties and its suitability for different aquatic species.
* **specific\_gravity** - It shows the specific gravity of the water, which is a dimensionless value indicating the density of the water relative to pure water. This value is affected by temperature, salinity, and other factors.
* **pressure\_abs** - It shows the absolute pressure in the water, (Bars). This value includes both the atmospheric pressure and the water pressure, useful for depth calculations.
* **depth** - It shows the depth of the water column, typically measured in meters (m). This value is derived from the pressure sensor and indicates how deep the sensor is below the water surface.
* **battery\_voltage** - It shows the voltage level of the sensor's battery, typically measured in volts (V). This value indicates the current power level of the sensor's battery.
* **battery\_soc** - It shows the state of charge (SOC) of the sensor's battery as a percentage (%). This value represents how much charge is left in the battery, with 100% being fully charged and 0% being fully depleted.

## Usage

### Opening Closing

* Unscrew pressure valve plug (blue) or insert vacuum adapter plug (red) to open the vent
  * so it's easier to remove or insert flanges

{% hint style="warning" %}
Ensure inside of the tube is grease as well as the o-rings

Areas cover with grease are clear out of any debris
{% endhint %}

{% hint style="danger" %}
Ensure no vacuum adapter is inserted before submerging
{% endhint %}

### Check sealing

It is recommended to check if it seals with manual vacuum pump before each submersion.&#x20;

Manual Vacuum pump MVM8900 \
[https://bluerobotics.com/store/watertight-enclosures/enclosure-tools-supplies/vacuum-pump-kit-r2-rp/](https://bluerobotics.com/store/watertight-enclosures/enclosure-tools-supplies/vacuum-pump-kit-r2-rp/)

[https://bluerobotics.com/learn/using-the-vacuum-test-plug/](https://bluerobotics.com/learn/using-the-vacuum-test-plug/)

### SD card

Remove or add SD card only when device is turned off.

### Config

File in the root directory "config.txt"

Default values

```cpp
LOGGING_DELAY=10000
BATTERY_ALARM_TH=20
BASELINE_ALTITUDE=384.0
DO_CALIBRATION=0.583250
```

Logging delay - milliseconds value for logging data period

Battery alarm threshold - battery percentage value to trigger an event (currently no event implemented). Battery value is displayed on OLED with other senor values as well as logged in the data files.

Baseline altitude - To be used only MS5803 Sensor is being used to calculate relative pressure. Currently MS5837 is used.

Dissolved oxygen calibration - Value of the sensor when sensor is outside water. Used as number for calculating % of dissolved oxygen.&#x20;

{% hint style="info" %}
DO\_CALIBRATION should be updated with the new value on location.
{% endhint %}

## Maintenance

### Sensors&#x20;

#### Turbidity

Clean with a soft sponge without damanging the plastic casing. Ensure there are no debris between two wings.

#### Conductivity

From [https://files.atlas-scientific.com/Mini\_EC\_K\_1.0\_probe.pdf](https://files.atlas-scientific.com/Mini\_EC\_K\_1.0\_probe.pdf)

<div>

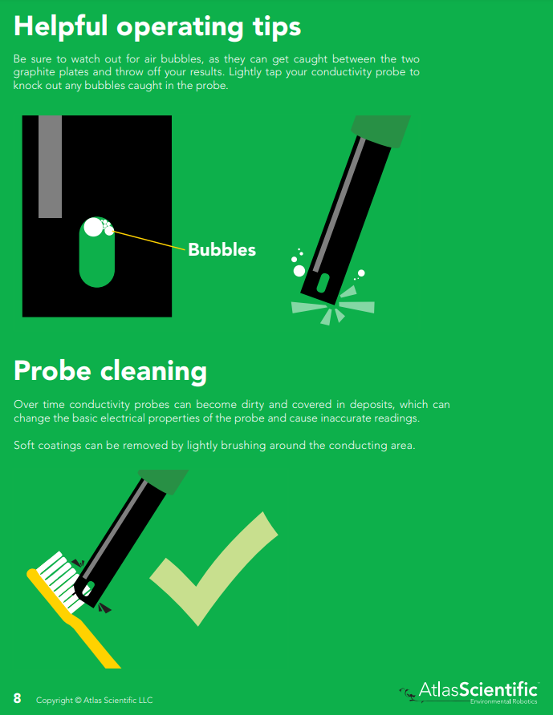
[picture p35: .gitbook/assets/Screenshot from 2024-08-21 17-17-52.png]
<figure><figcaption></figcaption></figure>

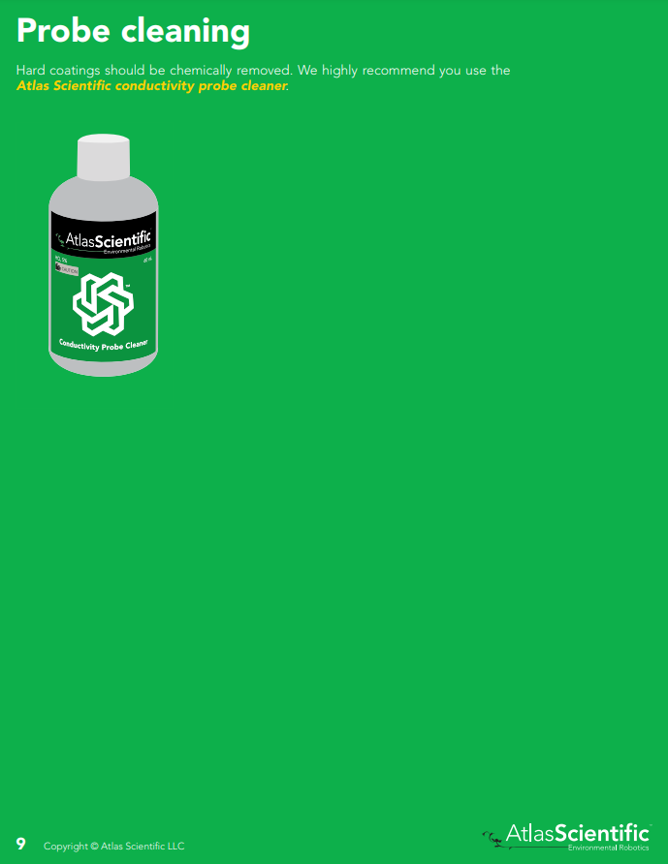
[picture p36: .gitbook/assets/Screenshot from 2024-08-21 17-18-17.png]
<figure><figcaption></figcaption></figure>

</div>

#### Dissolved oxygen

From [https://files.atlas-scientific.com/Mini\_DO\_probe.pdf](https://files.atlas-scientific.com/Mini\_DO\_probe.pdf)

<div>

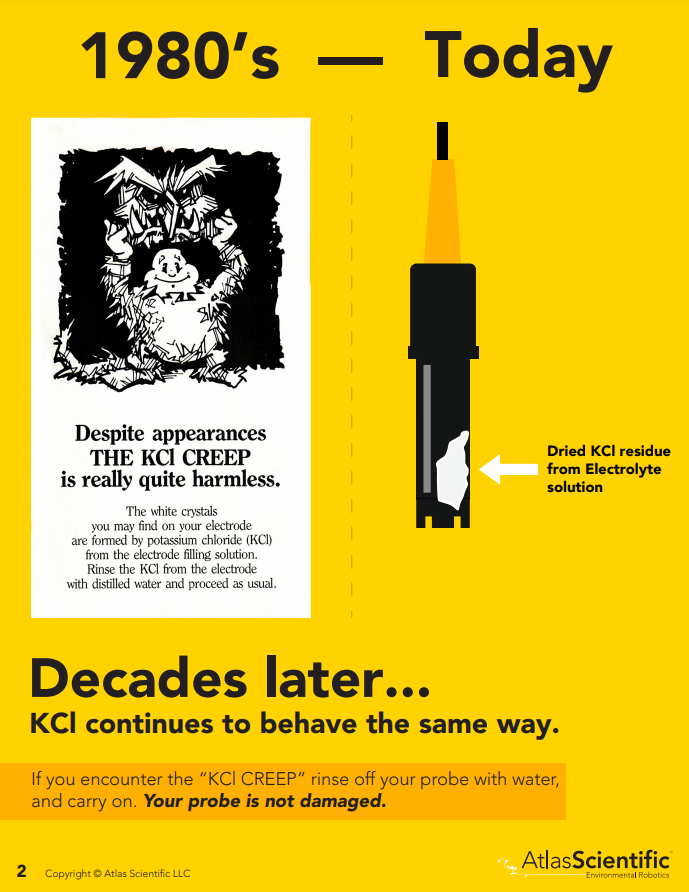
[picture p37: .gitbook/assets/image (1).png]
<figure><figcaption></figcaption></figure>

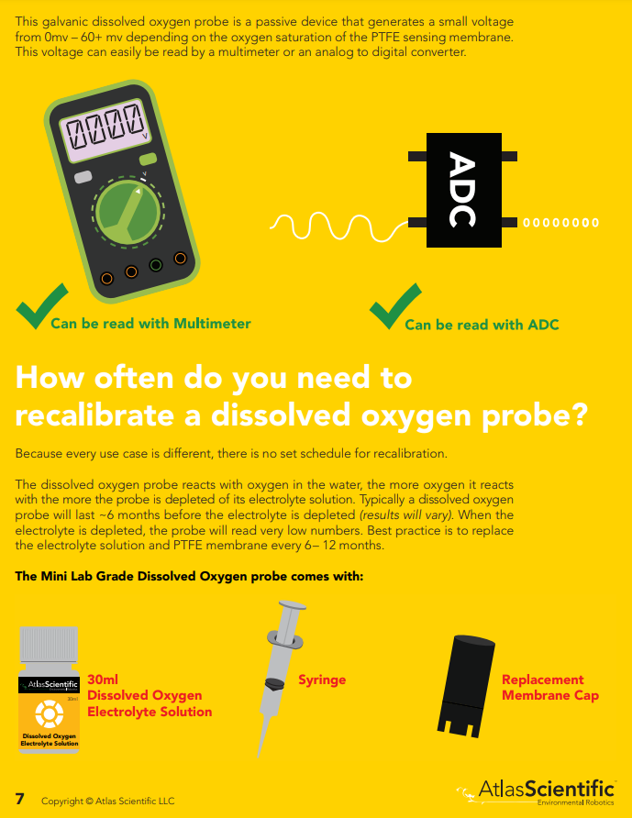
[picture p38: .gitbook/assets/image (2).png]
<figure><figcaption></figcaption></figure>

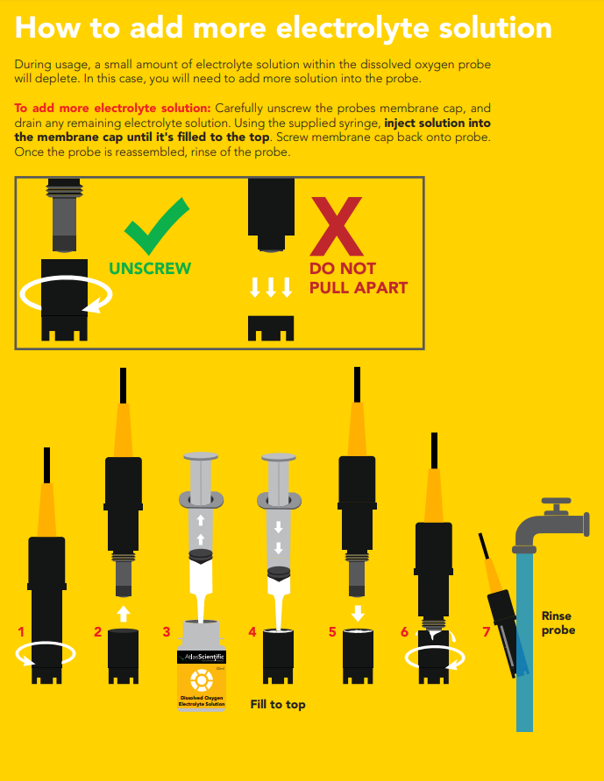
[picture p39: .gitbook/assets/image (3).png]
<figure><figcaption></figcaption></figure>

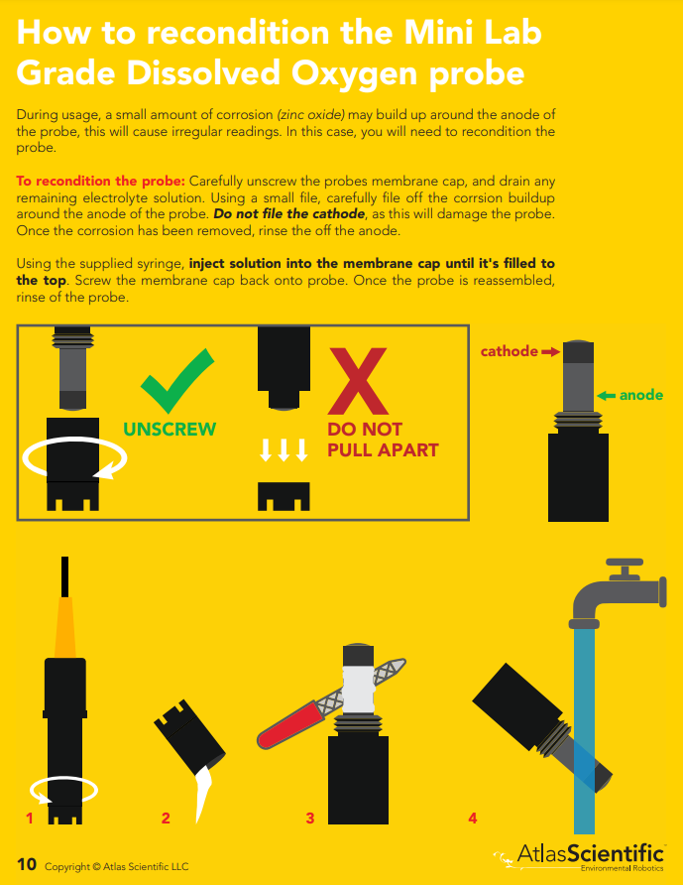
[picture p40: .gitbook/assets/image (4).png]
<figure><figcaption></figcaption></figure>

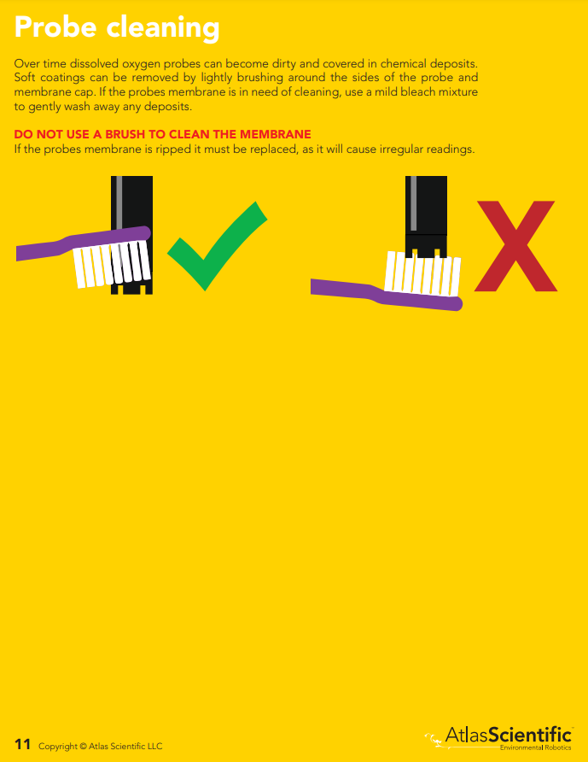
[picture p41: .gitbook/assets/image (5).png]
<figure><figcaption></figcaption></figure>

</div>

### O-rings

{% hint style="danger" %}
Use plastic tools, NOT steel or other hard tools, to remove the O-rings from the sealing flange. Hard tools can create scrapes that will compromise sealing ability.
{% endhint %}

{% hint style="danger" %}
Always inspect the O-rings before operation in water and especially when replacing the end-caps, aluminum flanges, or penetrators. Any dust, hair, or other particles can cause a leak.
{% endhint %}

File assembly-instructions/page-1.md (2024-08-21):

---
description: Preparation of sensors
---

# Sensors

ressure

<details>

<summary>MS583730BA01-50</summary>

**Components**

* Sensor [https://www.digikey.it/en/products/detail/te-connectivity-measurement-specialties/MS583730BA01-50/5629501?s=N4IgTCBcDaILIGUCsAOAzAdjQBgEIEFsBGAWiWxAF0BfIA](https://www.digikey.it/en/products/detail/te-connectivity-measurement-specialties/MS583730BA01-50/5629501?s=N4IgTCBcDaILIGUCsAOAzAdjQBgEIEFsBGAWiWxAF0BfIA)
* 3D printed casing
* Cable&#x20;
* SMD 0.1uF Capacitor
* o-ring
* Flexible Urethane 8800
  * Syringe to inject liquid inside casing

**Steps**

* 3D print
  * File name:
    * MS583730BA01-50-Enclosure\_inner
    * MS583730BA01-50- Enclosure\_outer
  * Print settings
    * 6 Layer walls
    * 100% infill
  * Material: PETG



* Solder capacitor and cable



* Apply conformal coating on soldering
* Install o-ring to sensor
* Clean cable with IPA
* Insert sensor to casing



* Mount external casing



* Apply tape on the end to prevent leaking



* Fill casing with Urethane (using syringe)



* Cure it

</details>

<details>

<summary>MS580314BA01-00</summary>

**Components**

* Sensor
* 3D printed
  * MS580314BA01-00-Enclosure\_inner
  * MS580314BA01-00 - Enclosure\_outer
* Cable
* Flexible Urethane 8800

**Steps**

* 3D print
  * 6 Layer walls
  * 100% infill
  * PETG



* Solder capacitor and cable
* Apply conformal coating
* Clean cable with IPA
* Insert sensor to casing



* Mount external casing
* Apply tape to prevent Urethane leaking



* Fill casing with Urethane
* Cure itdone



</details>

## Turbidity sensor

* Sensor [https://www.dfrobot.com/product-1394.html](https://www.dfrobot.com/product-1394.html)
* 3D printed Casing
  * File name: Turbidity\_Cover
  * Print settings:
    * 6 Layer wall
    * 100% infill
    * 10mm Brim width
  * Material: PETG

<figure><figcaption></figcaption></figure>

* Desolder JST connector

<div>

<figure><figcaption></figcaption></figure>

<figure><figcaption></figcaption></figure>

</div>

* Solder the cable
  * Red - VCC
  * Black - GND
  * Green - Signal

<figure><figcaption></figcaption></figure>

* Hot Glue the wires to keep them in place
* Fill hot glue around sensor are to seal it, preventing Urethane filling sensor are

<figure><figcaption></figcaption></figure>

* Install casing
* Fill with Urethane

<figure><figcaption></figcaption></figure>

## Temperature

### Assemble EZO™ Carrier Board

<div>

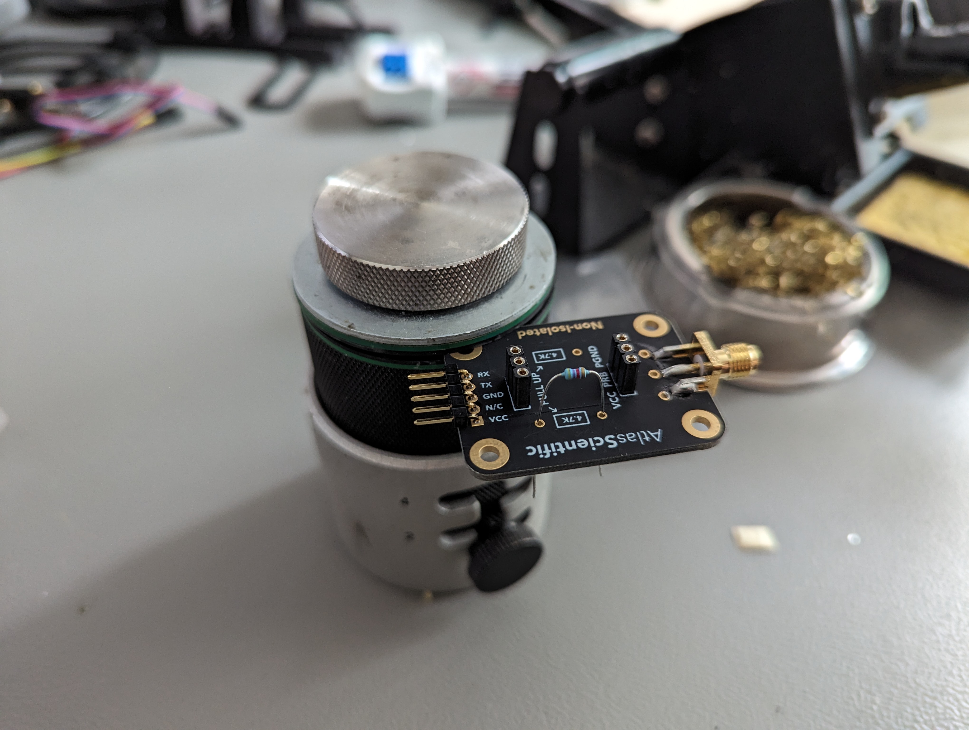
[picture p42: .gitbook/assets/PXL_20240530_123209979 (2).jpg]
<figure><figcaption></figcaption></figure>

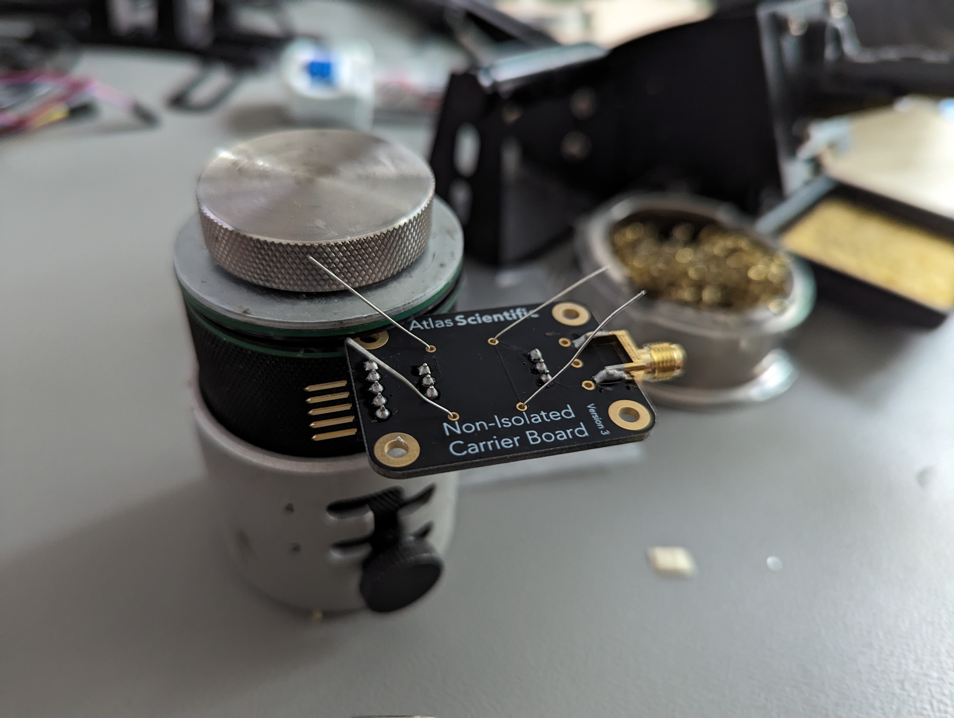
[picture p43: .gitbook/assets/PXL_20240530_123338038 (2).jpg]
<figure><figcaption></figcaption></figure>

</div>

<div>

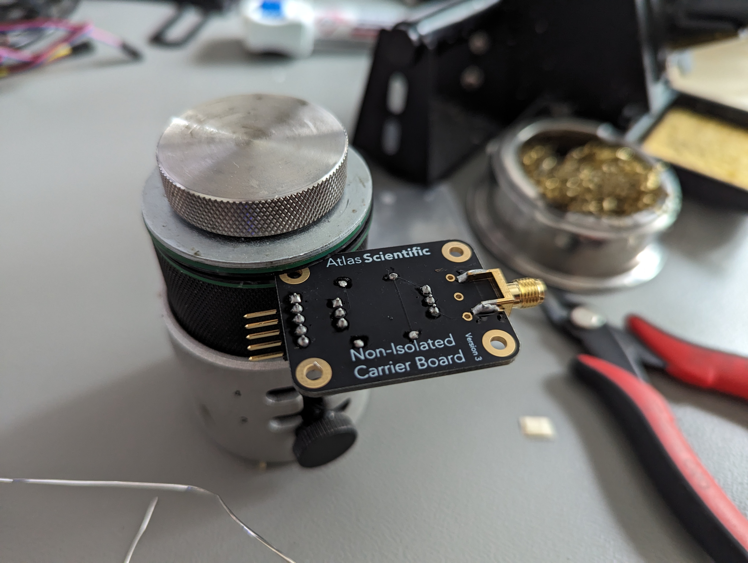
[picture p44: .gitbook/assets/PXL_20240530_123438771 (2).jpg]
<figure><figcaption></figcaption></figure>

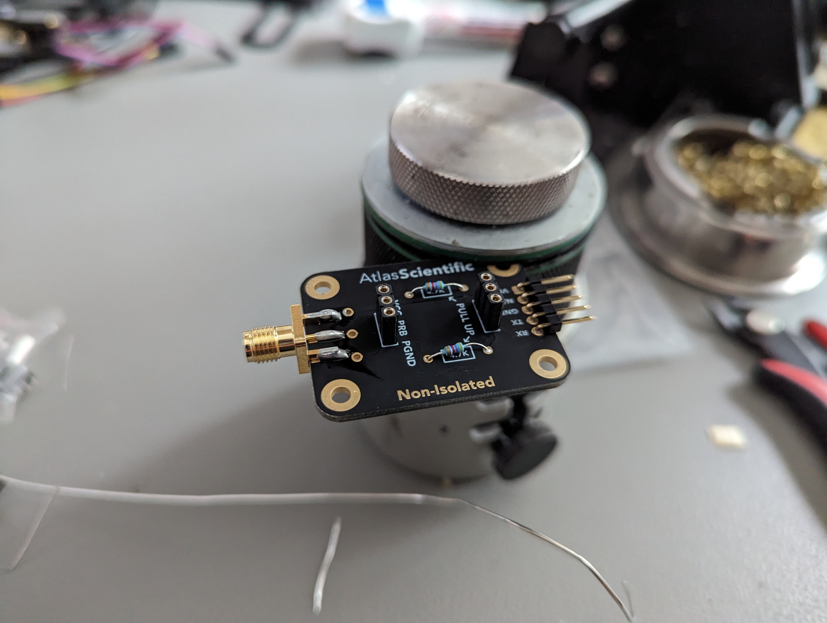
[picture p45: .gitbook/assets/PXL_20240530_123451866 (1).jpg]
<figure><figcaption></figcaption></figure>

</div>

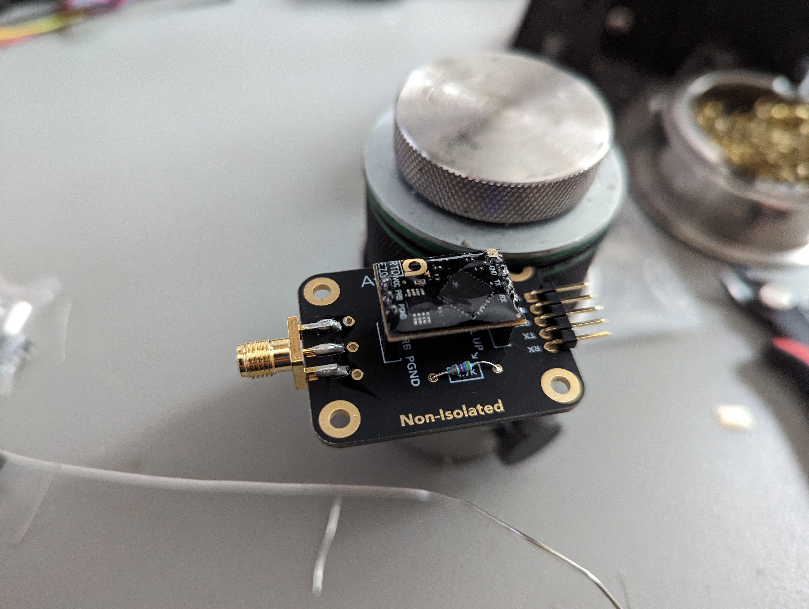
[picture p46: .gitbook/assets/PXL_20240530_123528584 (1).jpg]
<figure><figcaption></figcaption></figure>

### EZOboard I2C mode selection

{% hint style="warning" %}
Must change communication mode to I2c
{% endhint %}

It can be done easily buy connecting pins to the power source using jumper wires.\
Also, guide in here&#x20;

{% embed url="https://www.instructables.com/UART-AND-I2C-MODE-SWITCHING-FOR-ATLAS-SCIENTIFIC-E/" %}

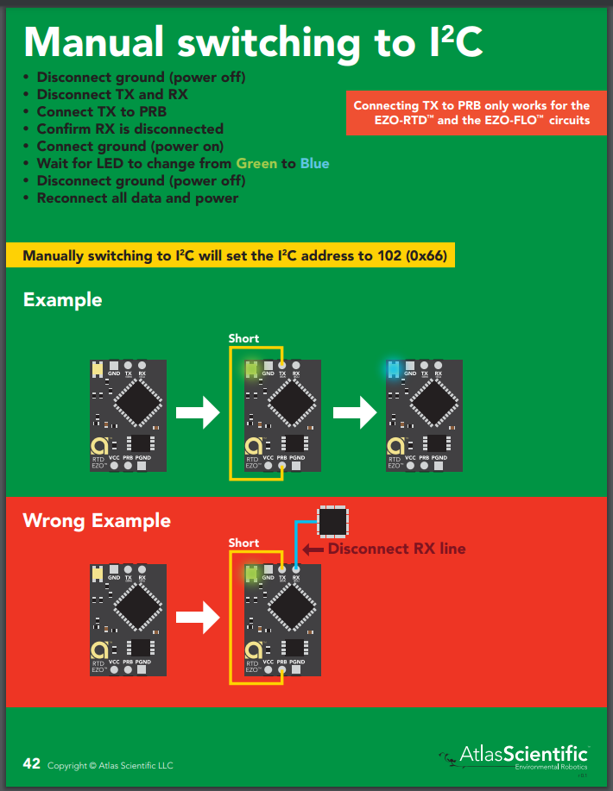
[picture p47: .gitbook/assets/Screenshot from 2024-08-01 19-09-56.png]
<figure><figcaption></figcaption></figure>

### Calibration

Using one of the Demos example send calibration command with known temperature

Best with boiling water at sea level for 100 degrees C

{% embed url="https://github.com/Atlas-Scientific/Ezo_I2c_lib/tree/master/Examples/I2c_lib_examples" %}

> **i2c\_scan\_and\_comms\_example:** scans the I2C line for an ezo device (lowest address thats on the line) and lets you send commands to it using the serial terminal. Use the "ADDR" command to change that devices' address.
>
> **iot\_cmd\_sample\_code:** large example that demonstrates polling 3 devices for readings and also lets you send commands to any of them from the serial terminal. Use the "HELP" command for more details

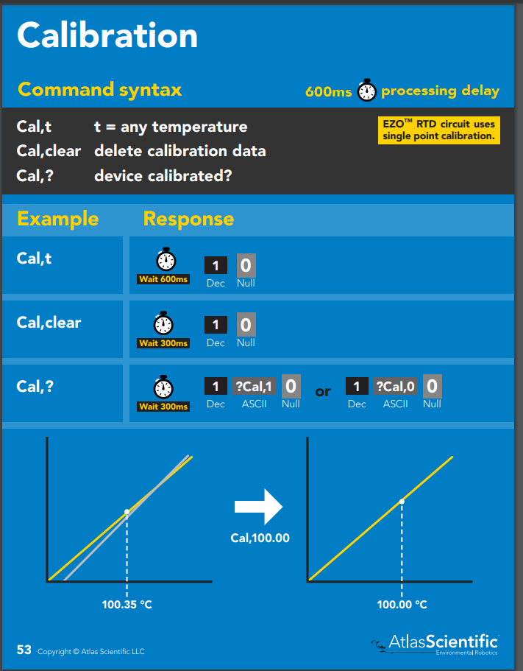
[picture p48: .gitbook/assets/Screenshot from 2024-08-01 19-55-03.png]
<figure><figcaption></figcaption></figure>

## Dissolved Oxygen

[https://files.atlas-scientific.com/Mini\_DO\_probe.pdf](https://files.atlas-scientific.com/Mini\_DO\_probe.pdf)

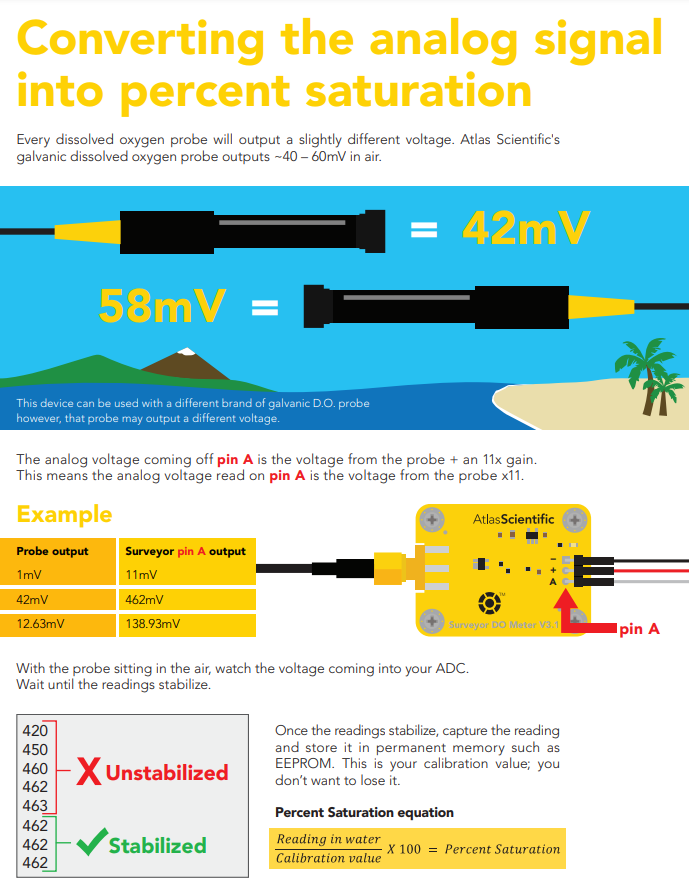
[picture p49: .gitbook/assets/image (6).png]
<figure><figcaption></figcaption></figure>

Enter value into the config file

## Conductivity

#### Change mode to to I2C

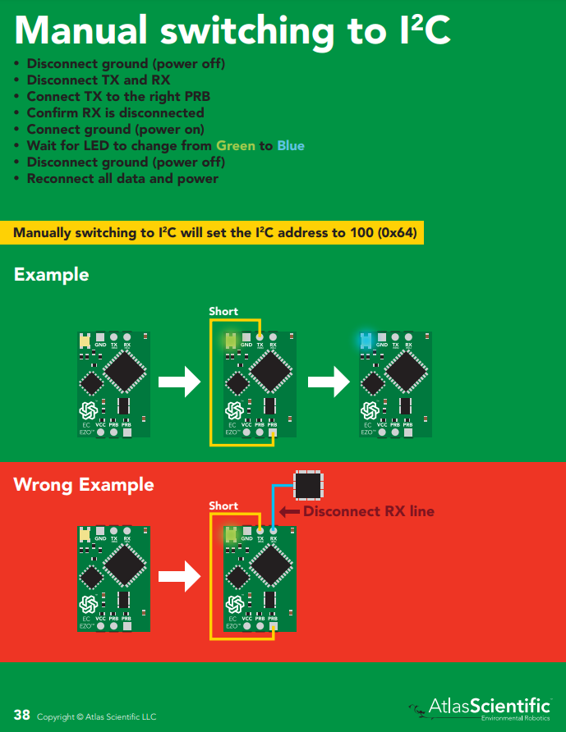
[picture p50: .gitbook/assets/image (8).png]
<figure><figcaption></figcaption></figure>

#### Calibration

{% embed url="https://github.com/Atlas-Scientific/Ezo_I2c_lib/tree/master/Examples/I2c_lib_examples" %}

> **i2c\_scan\_and\_comms\_example:** scans the I2C line for an ezo device (lowest address thats on the line) and lets you send commands to it using the serial terminal. Use the "ADDR" command to change that devices' address.
>
> **iot\_cmd\_sample\_code:** large example that demonstrates polling 3 devices for readings and also lets you send commands to any of them from the serial terminal. Use the "HELP" command for more details

1. Add probe directly into a solution bag
2. Send command&#x20;

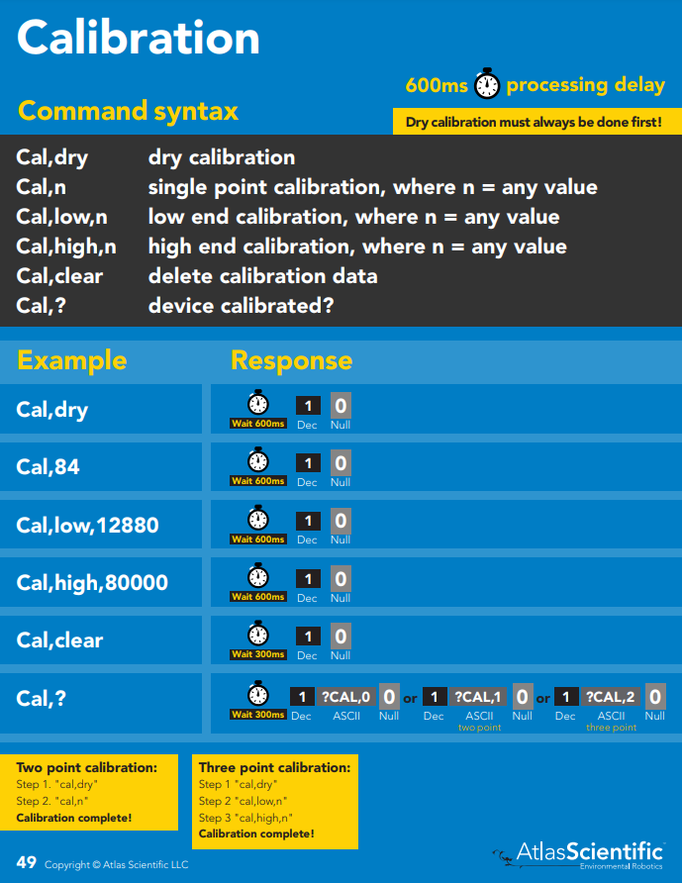
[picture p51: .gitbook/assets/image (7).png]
<figure><figcaption></figcaption></figure>

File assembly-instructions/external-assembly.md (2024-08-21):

# External assembly

## Tube clamps

1. Fix 2x Top clamps with the handle with 2x M3x10 screws
2. Fix Clamps around the tube with 8x M3x10 Screws

<div>

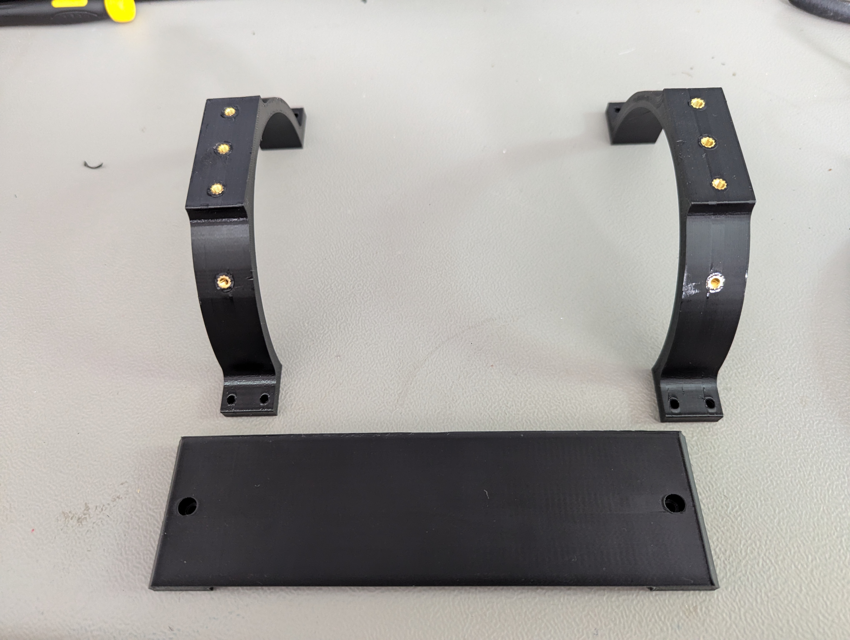
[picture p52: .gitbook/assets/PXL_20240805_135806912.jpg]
<figure><figcaption></figcaption></figure>

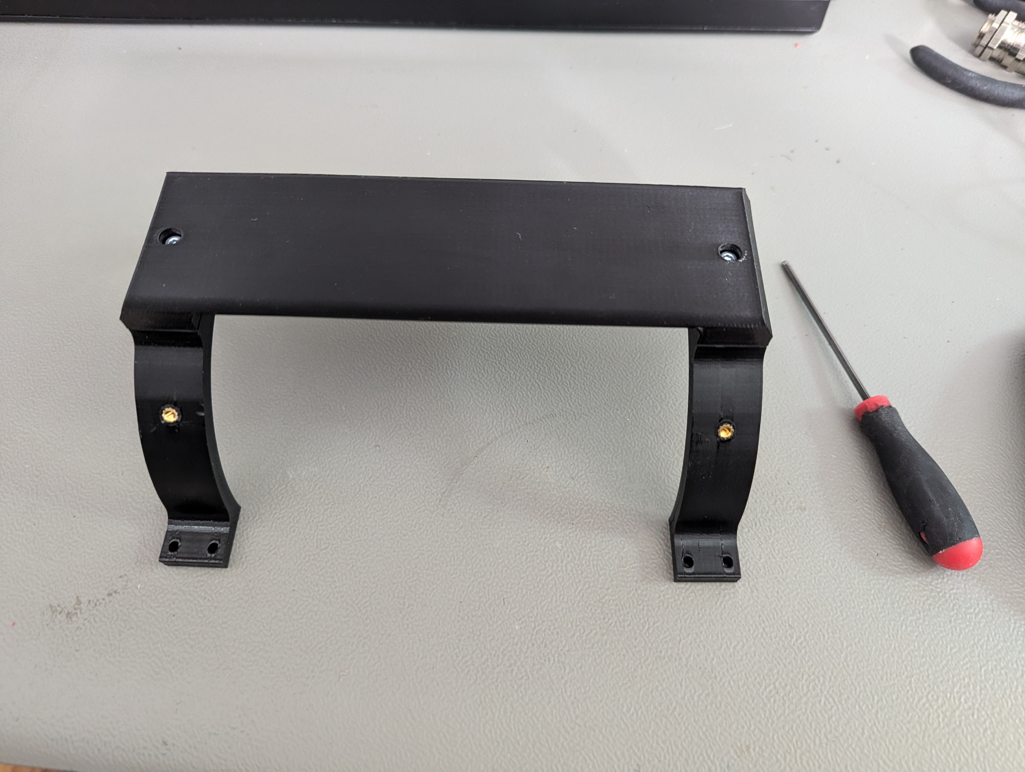
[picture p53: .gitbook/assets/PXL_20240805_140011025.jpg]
<figure><figcaption></figcaption></figure>

</div>

<div>

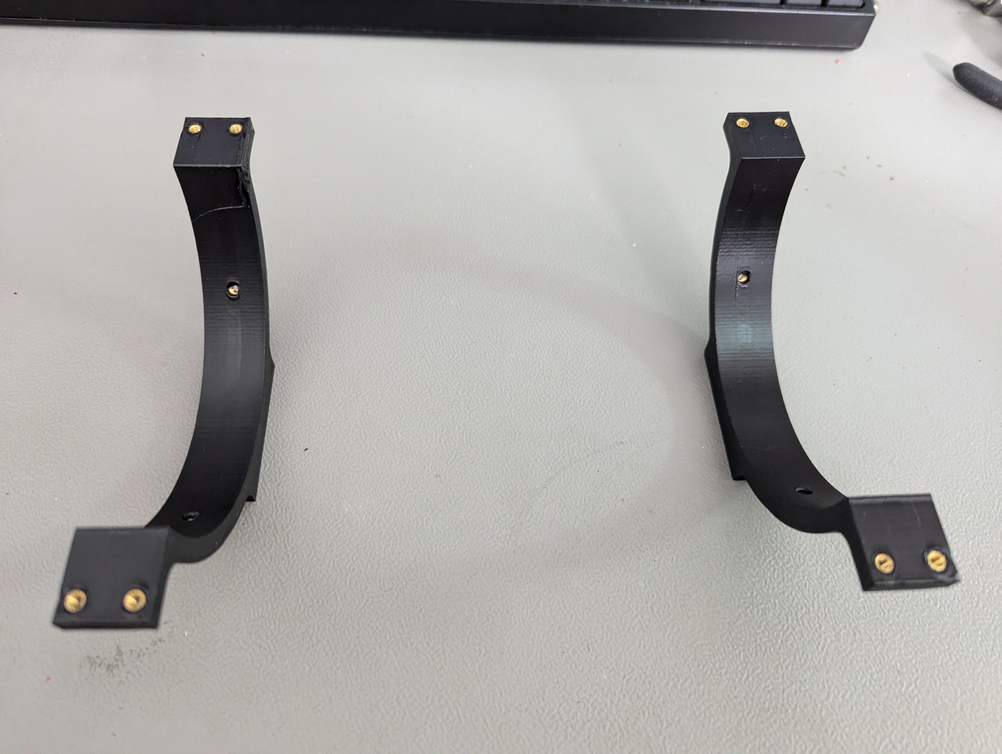
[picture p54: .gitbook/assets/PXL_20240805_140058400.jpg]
<figure><figcaption></figcaption></figure>

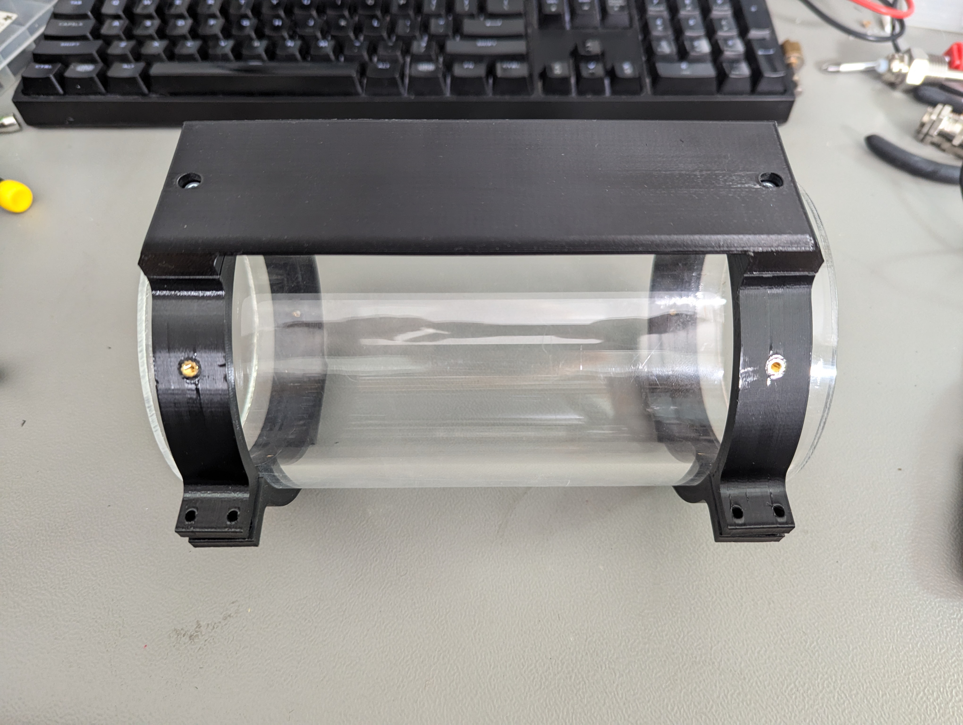
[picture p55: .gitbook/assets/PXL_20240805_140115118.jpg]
<figure><figcaption></figcaption></figure>

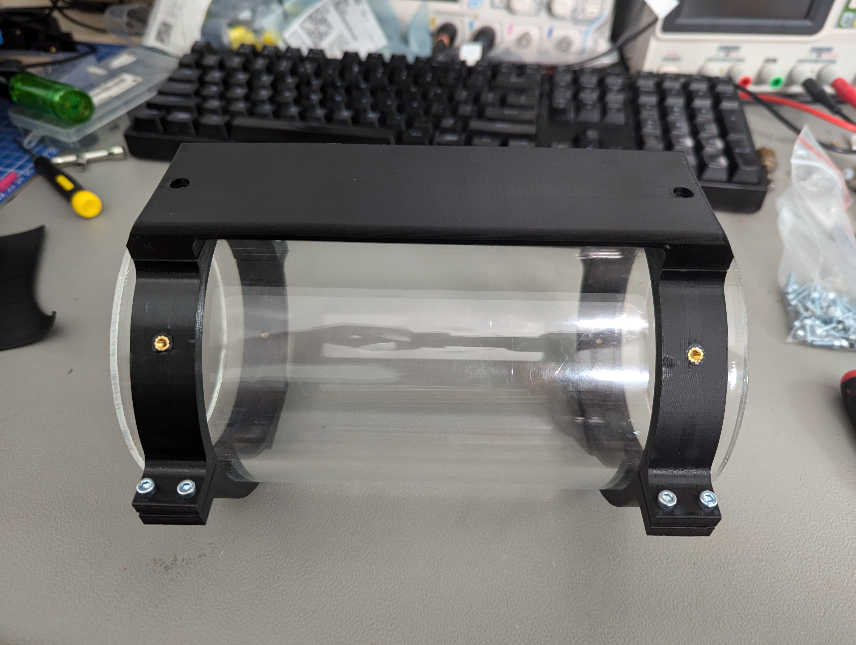
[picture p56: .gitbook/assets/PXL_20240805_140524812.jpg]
<figure><figcaption></figcaption></figure>

</div>

## Switch

1. Insert magnet into the slider
2. Insert spring to the switch casing
3. Insert slider to the switch casing
4. Install switch holders on bottom clamp with 2x M3x10 screws
5. Mount switch casing on the holders with 4x M3x10 screws

<div>

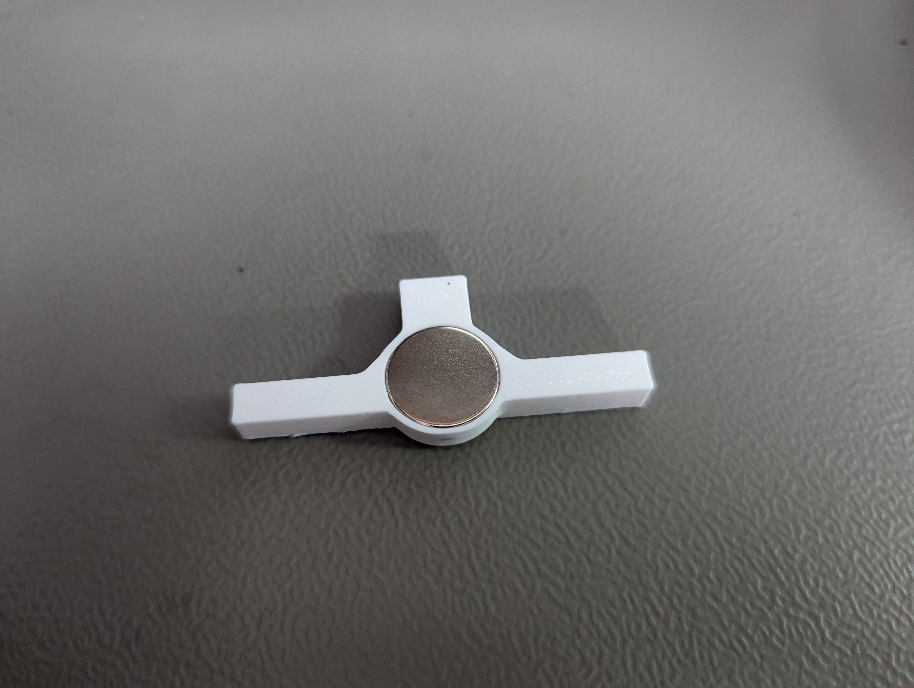
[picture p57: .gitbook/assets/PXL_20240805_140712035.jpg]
<figure><figcaption></figcaption></figure>

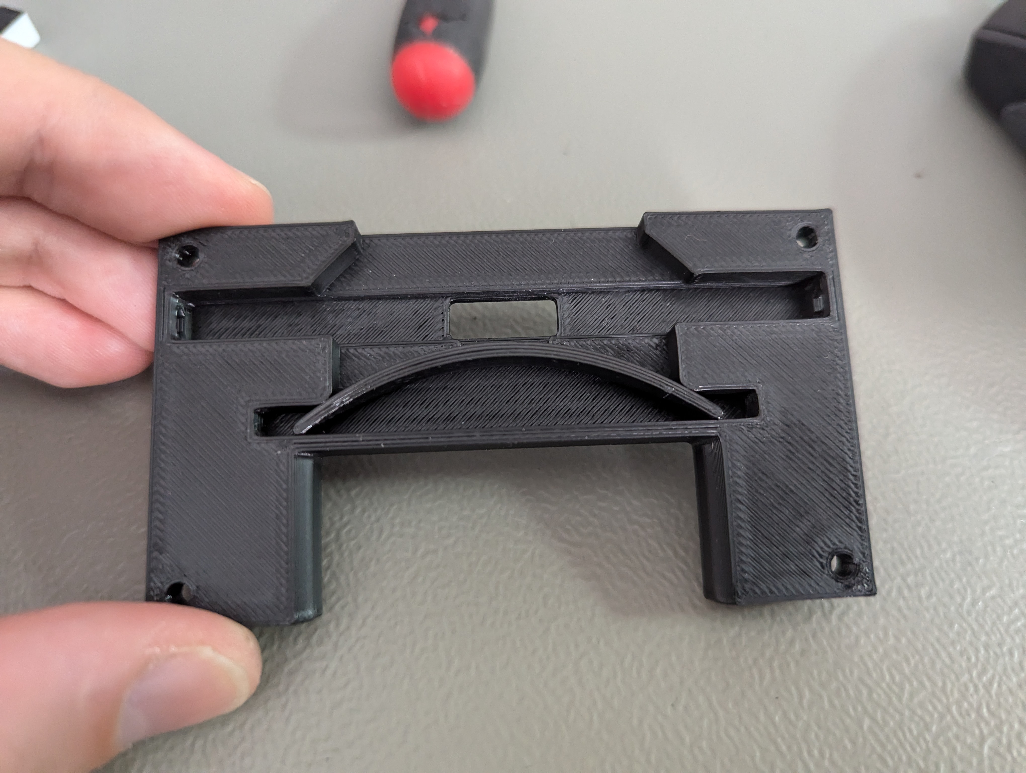
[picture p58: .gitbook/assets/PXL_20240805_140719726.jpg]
<figure><figcaption></figcaption></figure>

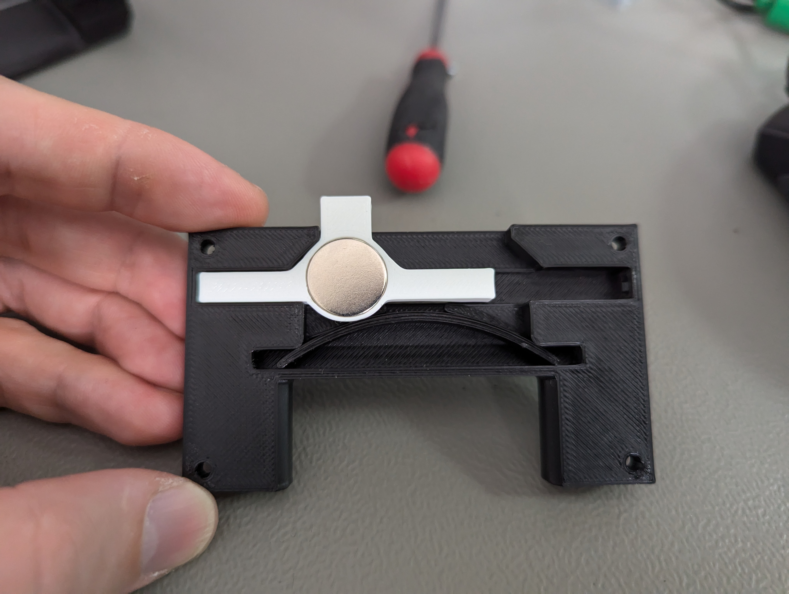
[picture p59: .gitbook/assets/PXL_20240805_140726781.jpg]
<figure><figcaption></figcaption></figure>

</div>

<div>

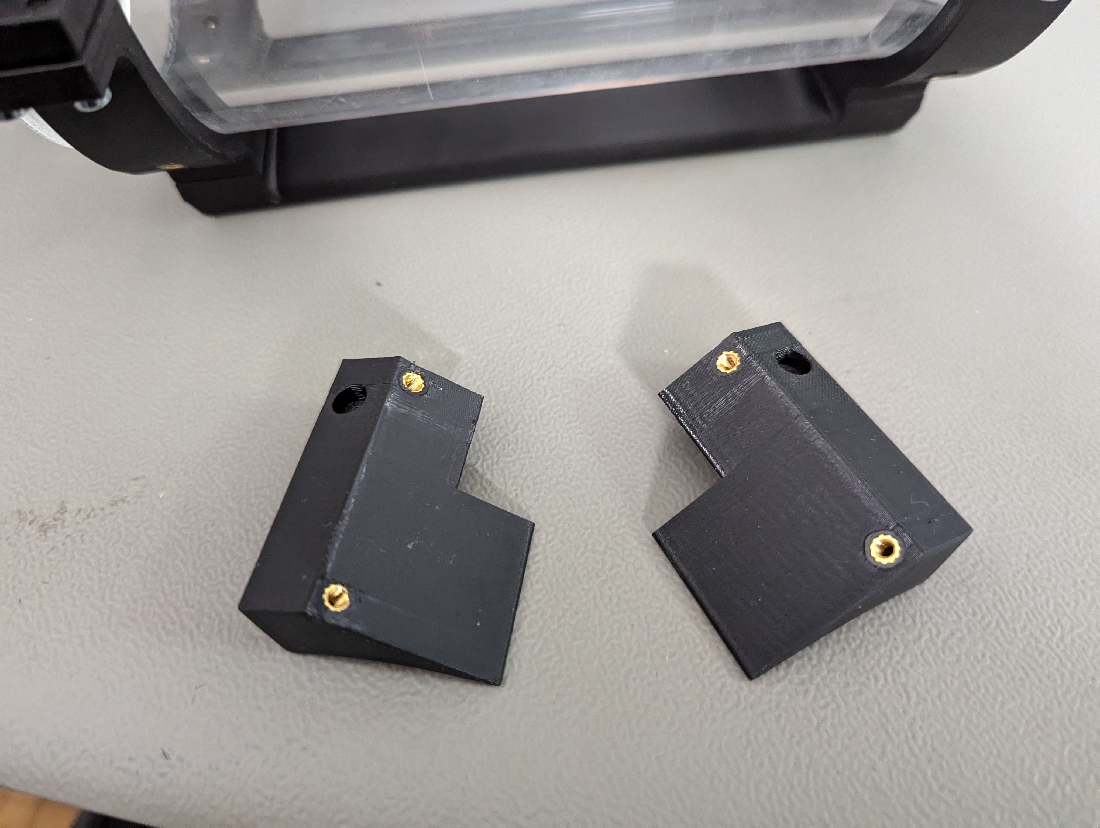
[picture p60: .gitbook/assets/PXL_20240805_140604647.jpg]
<figure><figcaption></figcaption></figure>

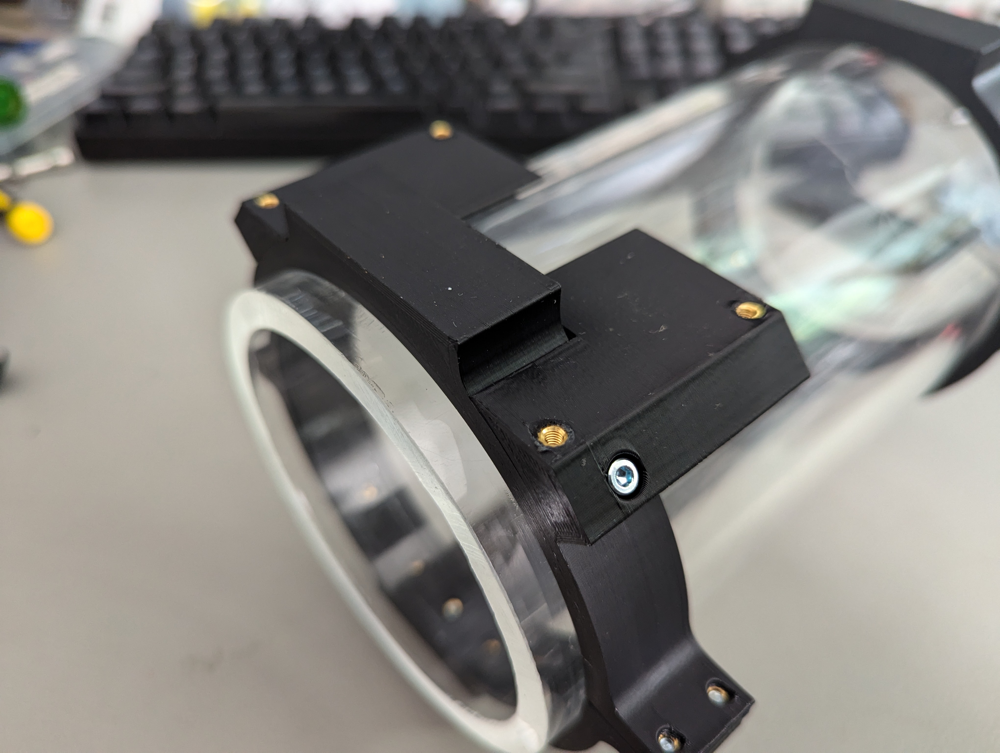
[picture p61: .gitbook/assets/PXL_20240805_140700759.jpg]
<figure><figcaption></figcaption></figure>

</div>

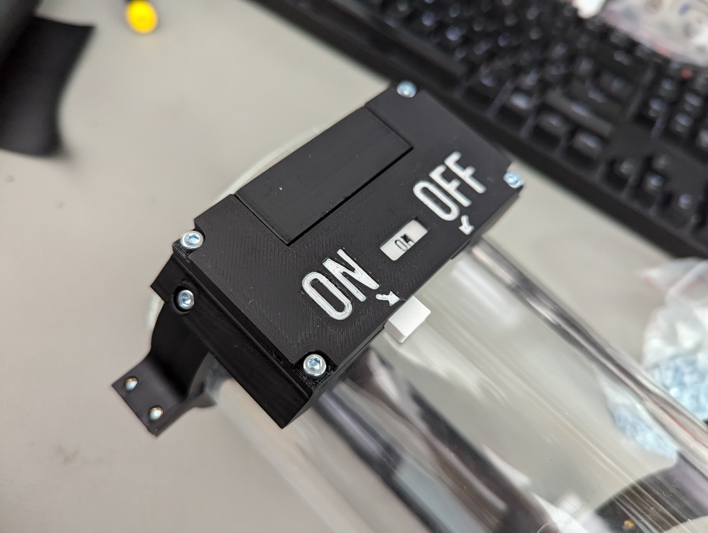
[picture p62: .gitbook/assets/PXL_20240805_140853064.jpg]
<figure><figcaption></figcaption></figure>

## Sensor holder and cover

1. Cut neoprene rubber piece to cover most of the are unsuring mounting holes are covered
2. Using 5x M3x6 screw fix if the the sensor holder
3. Cut a cross in each sensor holder location
4. Install sensor holder to the sensor cover
5. Prepare knobs
   1. Insert M3x20 Hex head bolts into the knobs
   2. User nut from the oposite side to pull it out

<div>

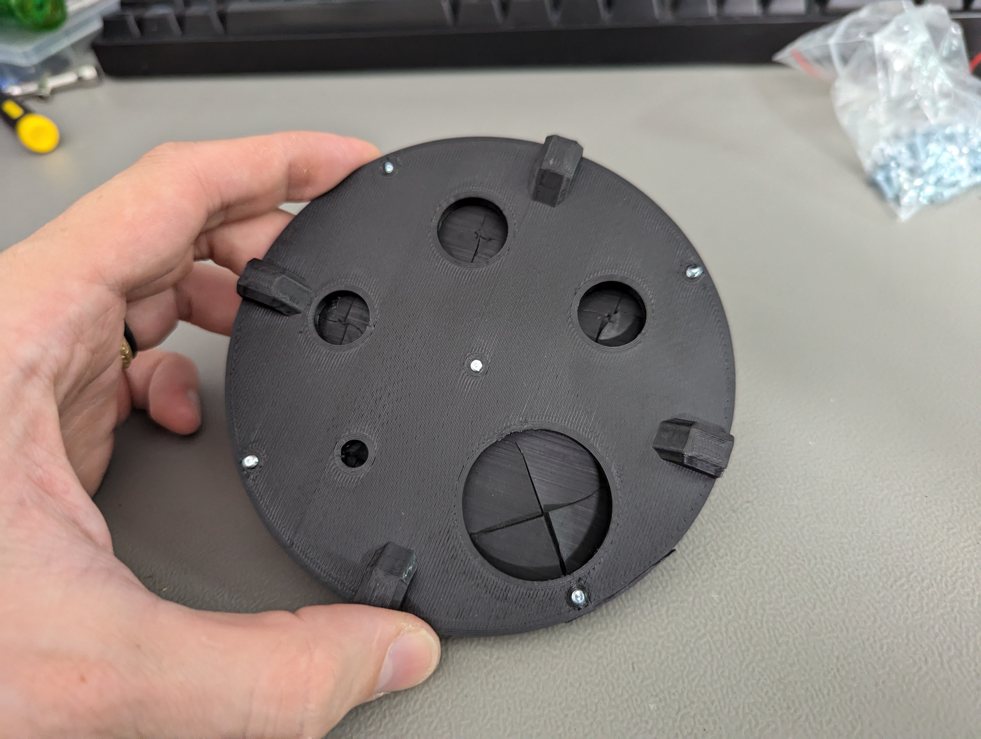
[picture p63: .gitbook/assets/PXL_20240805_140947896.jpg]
<figure><figcaption></figcaption></figure>

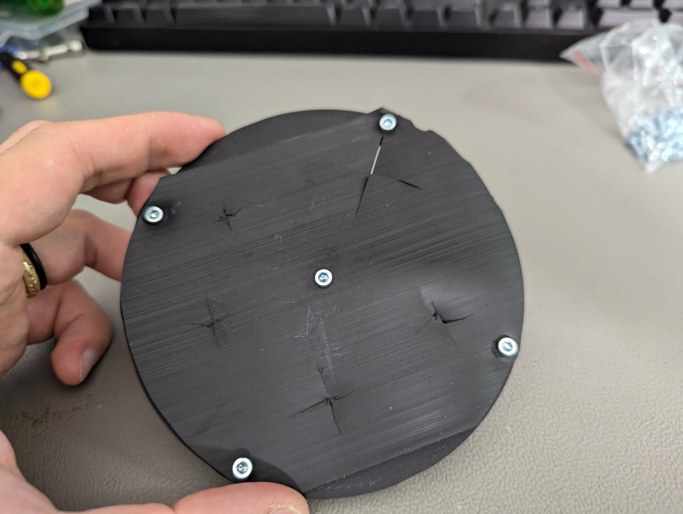
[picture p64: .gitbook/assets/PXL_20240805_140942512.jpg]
<figure><figcaption></figcaption></figure>

</div>

<div>

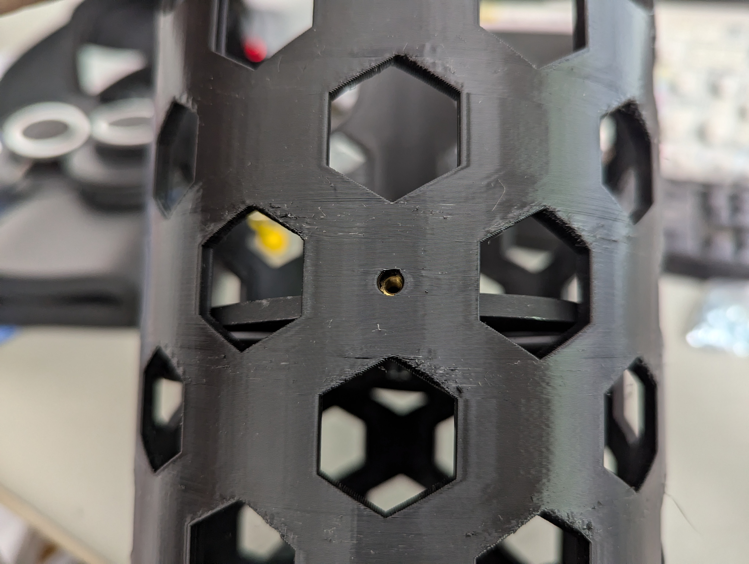
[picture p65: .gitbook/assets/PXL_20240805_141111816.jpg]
<figure><figcaption></figcaption></figure>

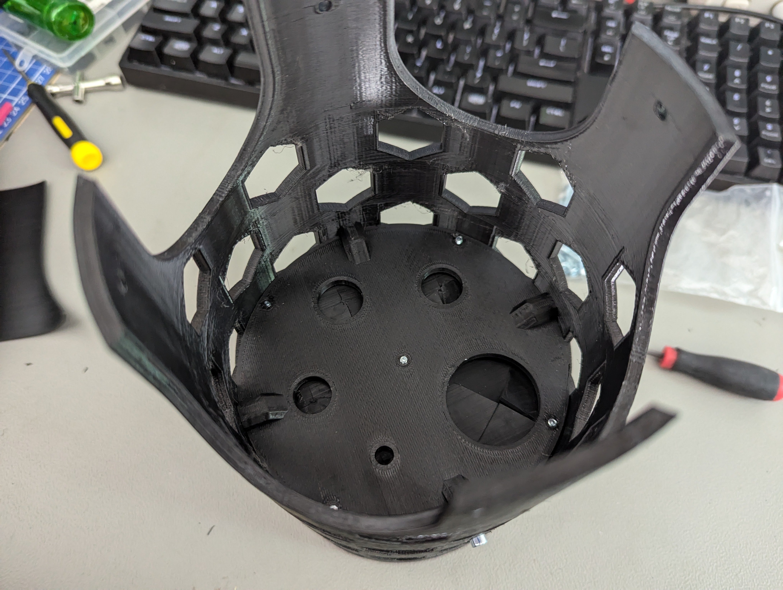
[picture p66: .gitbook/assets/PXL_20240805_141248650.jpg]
<figure><figcaption></figcaption></figure>

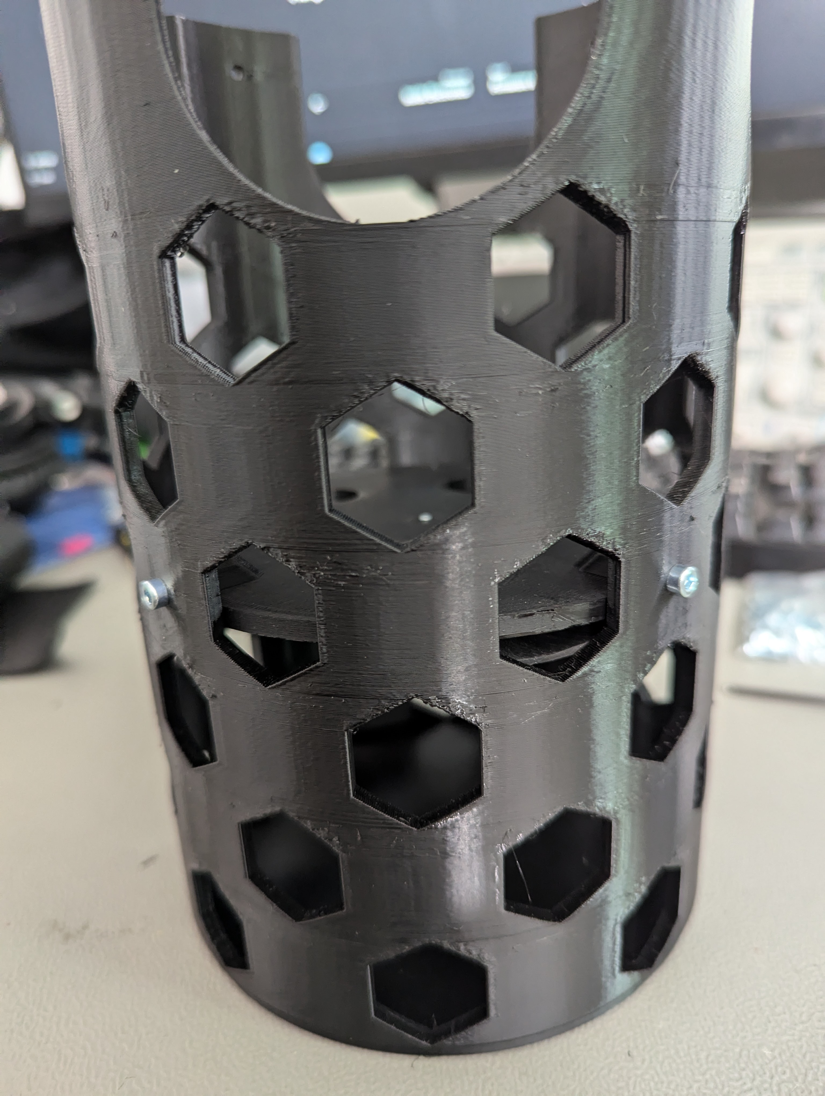
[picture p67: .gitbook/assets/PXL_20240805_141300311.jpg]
<figure><figcaption></figcaption></figure>

</div>

<div>

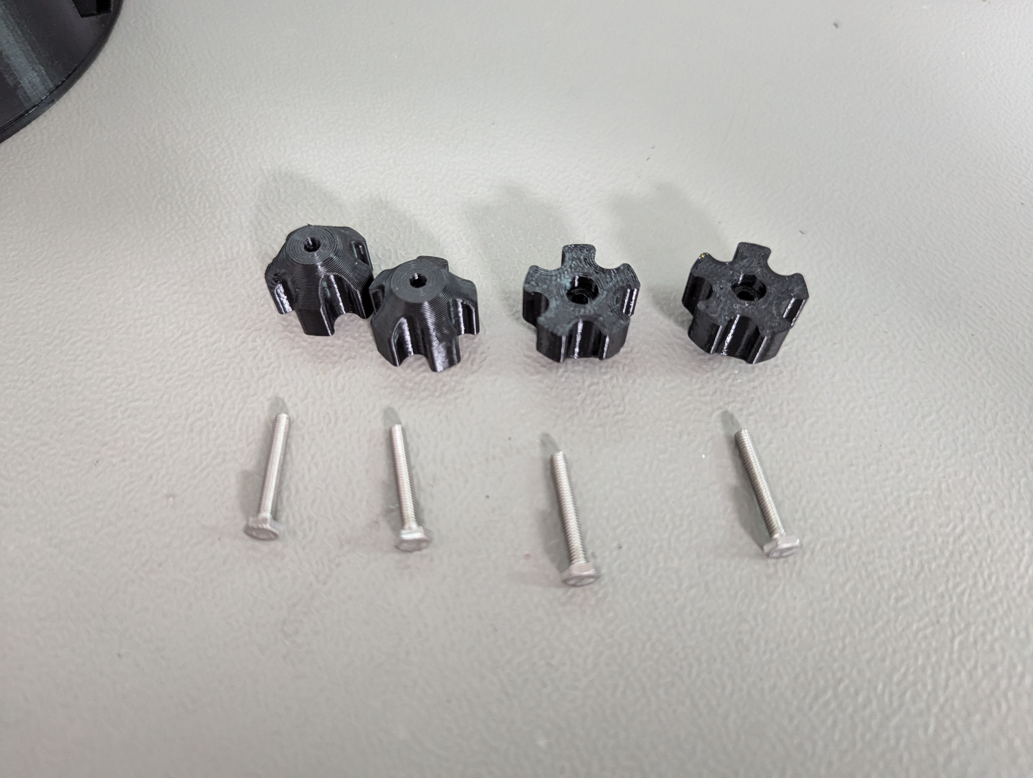
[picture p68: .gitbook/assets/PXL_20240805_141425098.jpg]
<figure><figcaption></figcaption></figure>

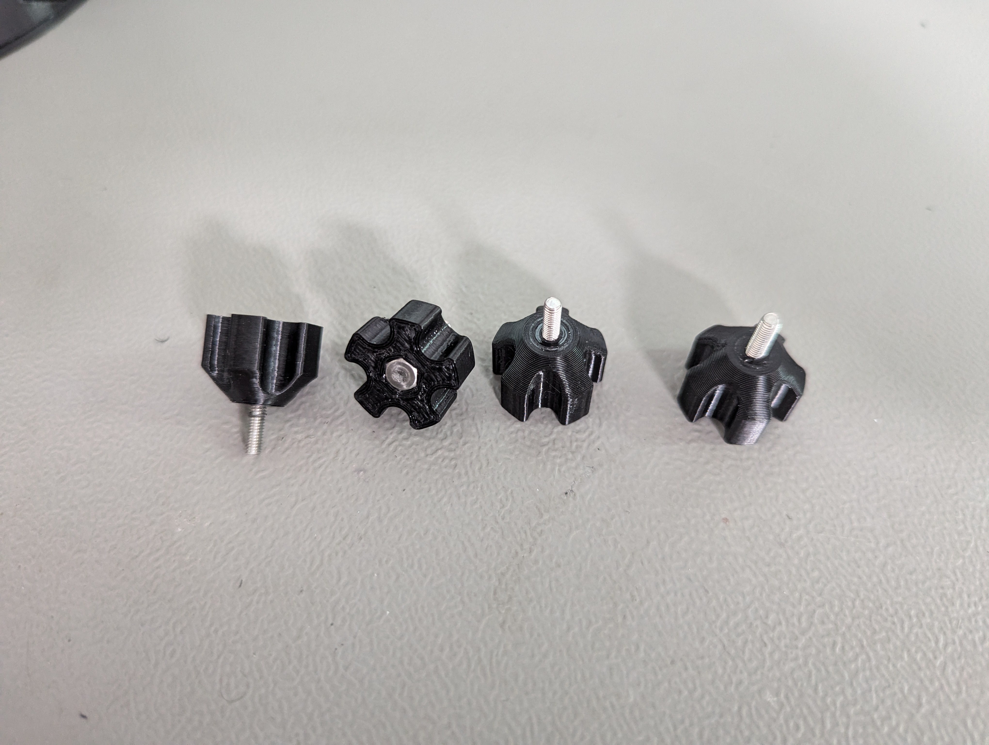
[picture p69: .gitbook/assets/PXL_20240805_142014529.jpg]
<figure><figcaption></figcaption></figure>

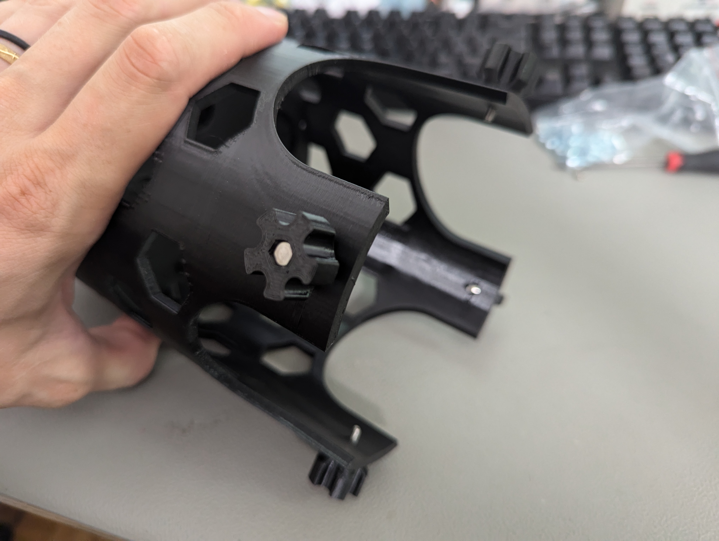
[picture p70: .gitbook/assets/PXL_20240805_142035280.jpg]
<figure><figcaption></figcaption></figure>

</div>

## Flanges

### Install cable glands

Flange colored black indicates the starting point, going clock wise. Surface with more deformities should be on the top. Order for installation:

1. RTD temp
2. Pressure
3. EC
4. Turb
5. OD

Steps:

1. Clean the cable gland threads&#x20;
2. Add Sikaflex 291i sealant around the threads&#x20;
3. Install the gland and tighten it. Would need 20 and 19mm Wrenches to hold.
4. Clean up excess sealant&#x20;
5. (optional) spray paint black for cleaner look

<div>

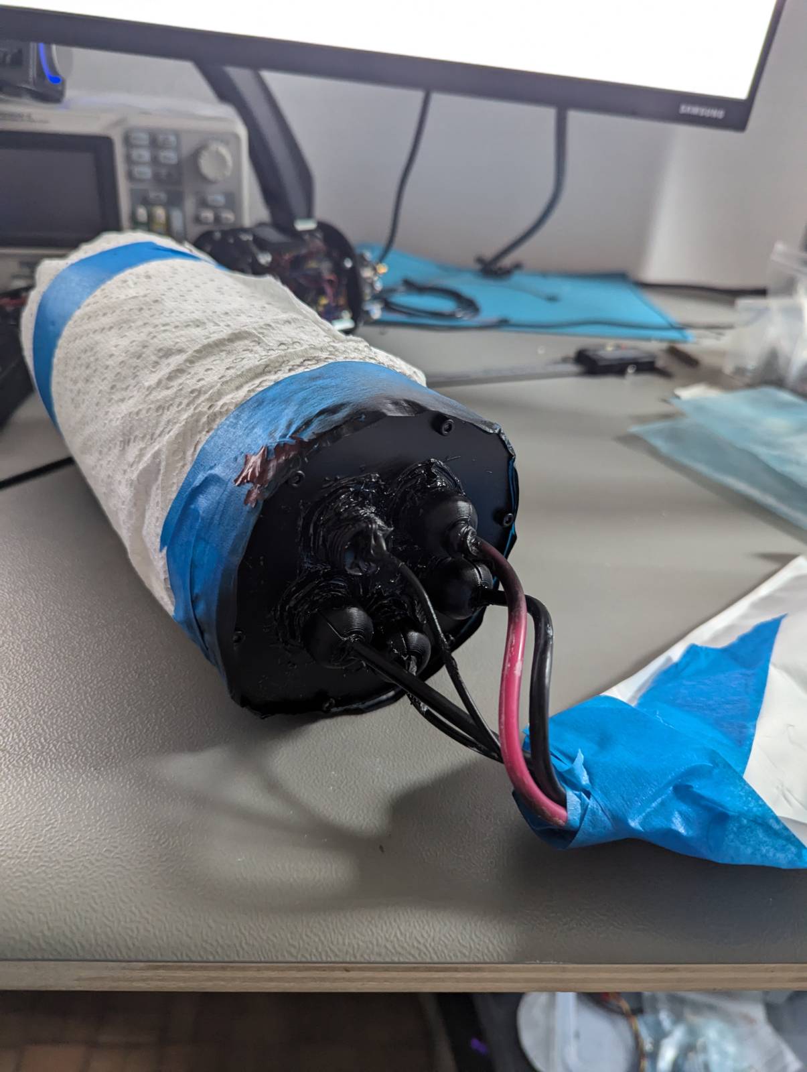
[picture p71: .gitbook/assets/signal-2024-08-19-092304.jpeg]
<figure><figcaption></figcaption></figure>

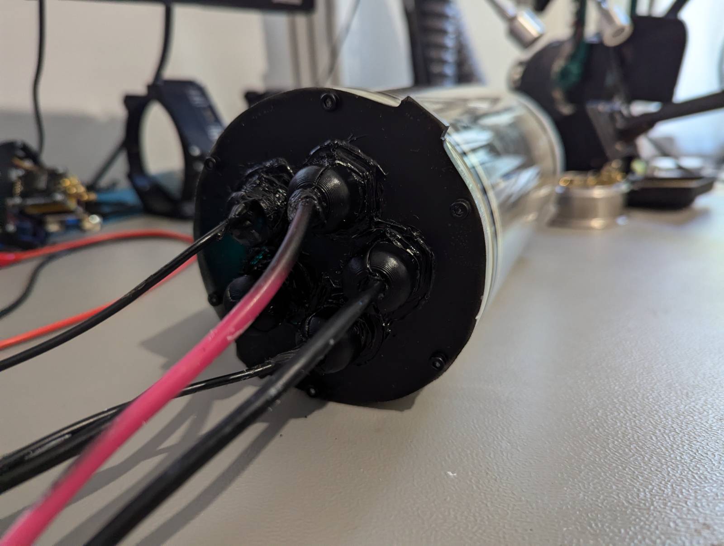
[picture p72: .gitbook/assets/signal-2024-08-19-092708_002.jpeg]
<figure><figcaption></figcaption></figure>

</div>

### Install Pressure relief valve

Indepth instructions follow here [https://bluerobotics.com/learn/pressure-relief-valve-installation-and-usage/](https://bluerobotics.com/learn/pressure-relief-valve-installation-and-usage/)

And for simpler vent [https://bluerobotics.com/learn/wte-vent-assembly-guide/](https://bluerobotics.com/learn/wte-vent-assembly-guide/)

1. Lubricate the o-ring
2. Install the pressure relief valve

<div>

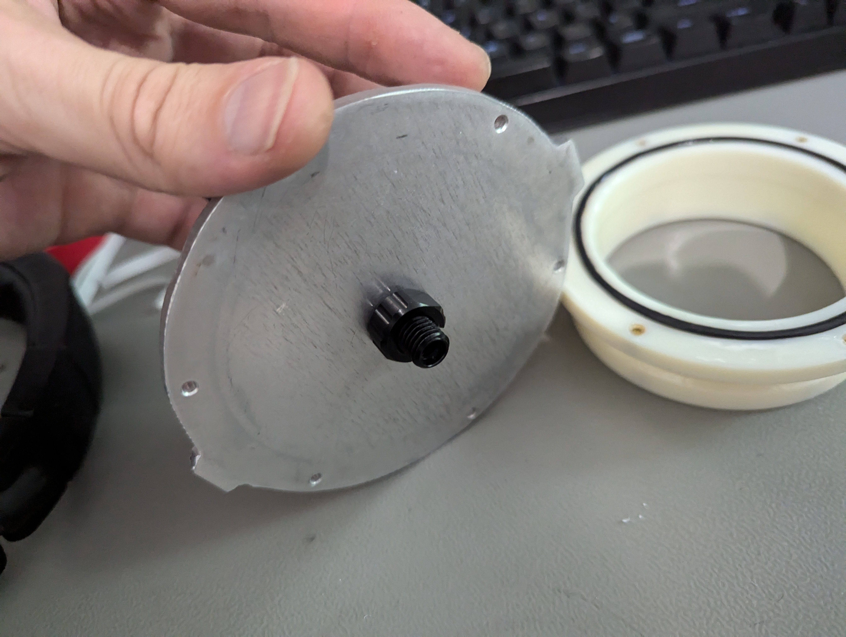
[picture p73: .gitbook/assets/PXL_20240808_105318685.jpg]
<figure><figcaption></figcaption></figure>

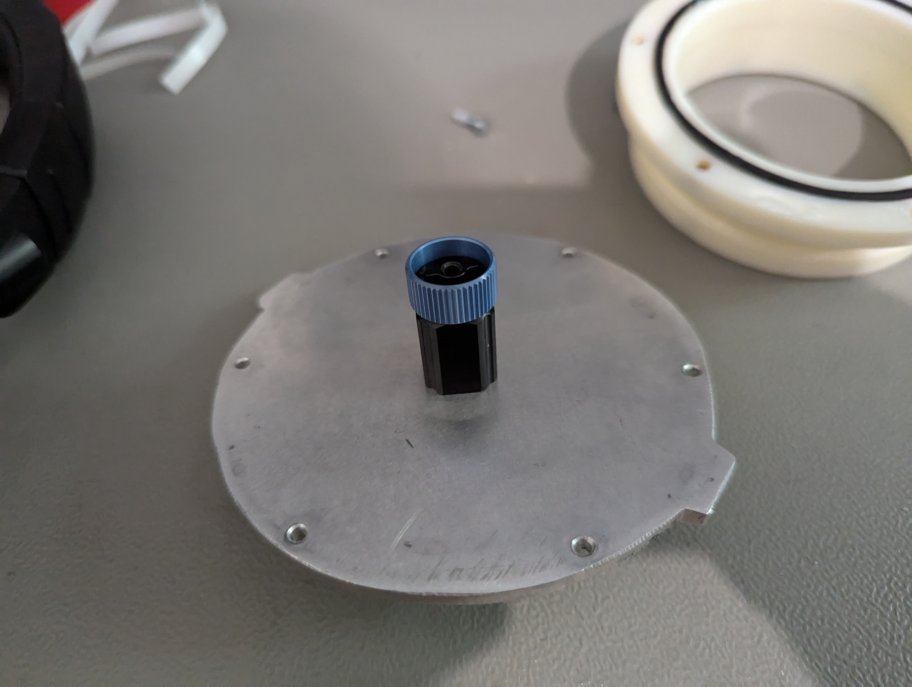
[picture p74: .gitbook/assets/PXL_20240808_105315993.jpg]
<figure><figcaption></figcaption></figure>

</div>

### Install aluminium lids&#x20;

1. Lubricate the o-rings
2. Lubricate the channel
3. Insert all 6x  M3x10 screws but just to find the slot
4. Tighten all screws in a star pattern
   1. Don't over-tighten
   2. There might seem that there is a gap, but 3D printed part has a slight bend at the edge. Also, the o-ring doesn't compresss completely.
5. Repeat for both sensors cable gland side and pressure relief side.

<div>

<figure><figcaption></figcaption></figure>

<figure><figcaption></figcaption></figure>

</div>

### Install O-rings to Flanges

1. Lubricate o-rings 90mm ID o-rings with grease
2. Lubricate the channel
3. Install on the sides

<figure><figcaption></figcaption></figure>

### Connecting Flange with Electronics

1. Install 3x3x M3x20mm standoffs
   1. Note position relating the flange lip
2. Connect sensors&#x20;
3. Connect standoffs with mounting ring with 3x M3x10mm screws

<div>

<figure><figcaption></figcaption></figure>

<figure><figcaption></figcaption></figure>

<figure><figcaption></figcaption></figure>

</div>

### Installing flanges

1. Install Sensor flange, ensure switch lines up
   1. If no clamps are present. Install clamps with the switch
2. Install sensors to sensor holder
3. Fix sensor holder to clamps
4. Install pressure relief valve flange
5. Test power switch

<div>

<figure><figcaption></figcaption></figure>

<figure><figcaption></figcaption></figure>

<figure><figcaption></figcaption></figure>

</div>

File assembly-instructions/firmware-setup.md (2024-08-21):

# Firmware setup

## Firmware setup

### IDE setup

1. Install Visual Studio code - [https://code.visualstudio.com/](https://code.visualstudio.com/)
2. Setup PlatformIO with dependencies as VSCode extension [https://platformio.org/install/ide?install=vscode](https://platformio.org/install/ide?install=vscode)
3. USB permissions
4. (Optional) if USB device not found remove "apt remove brltty"

Depending on IDE need to manually configure to download mode, or press buttons on the board to change mode

### Programming RTC

{% embed url="https://learn.adafruit.com/adafruit-ds3231-precision-rtc-breakout/arduino-usage" %}

Time set to UTC. As in the example compiling device timezone was UTC+2, therefore subtracted 7200 seconds to store UTC 0

```arduino
// Date and time functions using a DS3231 RTC connected via I2C and Wire lib
#include "RTClib.h"

RTC_DS3231 rtc;

void setup () {
  Serial.begin(115200);

  if (! rtc.begin()) {
    Serial.println("Couldn't find RTC");
    Serial.flush();
    while (1) delay(10);
  }

   if (rtc.lostPower()) {
     Serial.println("RTC lost power, let's set the time!");
     // When time needs to be set on a new device, or after a power loss, the
     // following line sets the RTC to the date & time this sketch was compiled
     // Get compile time
    DateTime compileTime(F(__DATE__), F(__TIME__));
    // Subtract 2 hours (7200 seconds)
    DateTime adjustedTime = compileTime - TimeSpan(7200);
    // Adjust the RTC time
    rtc.adjust(adjustedTime);
}

void loop () {
}
```

## Development notes

### I2C addresses

* 0x36 - MAX17048 - Fuel Gauge, Battery monitoring (on dev board)
* 0x48 - ADS1115 - ADC
* 0x49 - ADS1115 - (If A0/Addrees pin Soldered to HIGH) - ADC
* 0x64 - EZO-EC - Embedded Conductivity Circuit
* 0x66 - EZO-RTD Embedded Temperature Circuit
* 0x76 - MS5803-14BA - Pressure sensor

Can use Adafruit TestBed > I2CScan example to test/detect all I2C devices. [https://learn.adafruit.com/scanning-i2c-addresses/arduino-using-testbed](https://learn.adafruit.com/scanning-i2c-addresses/arduino-using-testbed)

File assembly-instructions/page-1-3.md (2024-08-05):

# Inside Electronics

## Sensor stack

1. Add EZOisolated EC board to SensorStackHolder
2. Mount 4x 12mm standoffs
3. Add Dissolved oxygen board
4. Mount 4x 12mm standoffs
5. Mount Non isolated Ezo board and 4x  M3x6 screw to fix it
6. Mount 2x 6mm standoffs on the side
7. Install Turbidity breakout with 2x M3x6 bolts

<div>

<figure><figcaption></figcaption></figure>

<figure><figcaption></figcaption></figure>

</div>

<div>

<figure><figcaption></figcaption></figure>

<figure><figcaption></figcaption></figure>

</div>

<div>

<figure><figcaption></figcaption></figure>

<figure><figcaption></figcaption></figure>

</div>

<figure><figcaption></figcaption></figure>

## Bottom ring

1. Install 2x M2.5x6mm Nylon standoffs on the ring
2. Add ADS1115 and fix it with bolts
3. Slide in 2x Qwiic adapter boards
4. Pre assemle 2x M3x10 mounting screws to SensorAttachmentHolder
5. Install SensorAttachmentHolder to the bottom ring
6. Slide in Qwiic adapter board to the SensorAttachmentHolder

<div>

<figure><figcaption></figcaption></figure>

<figure><figcaption></figcaption></figure>

</div>

<div>

<figure><figcaption></figcaption></figure>

<figure><figcaption></figcaption></figure>

</div>

<div>

<figure><figcaption></figcaption></figure>

<figure><figcaption></figcaption></figure>

</div>

1. Connect 2x EZOboards to Qwiic adapters with W4, W5 custom cables
2. Connect I2C interface using qwiic connectors in this order:
   1. Pressure sensor qwiic to ADS1115
      1. 50mm Cable
   2. ADS1115 tp Qwiicc adapter for EZO EC
      1. 50mm cable
   3. Qwiic adapter for EZO EC to EZO RTD
      1. 100mm cable

<div>

<figure><figcaption></figcaption></figure>

<figure><figcaption></figcaption></figure>

</div>

<div>

<figure><figcaption></figcaption></figure>

<figure><figcaption></figcaption></figure>

<figure><figcaption></figcaption></figure>

</div>

## Battery holder

1. Install 4x M3 20mm standoffs on the sides
2. Install 2x M3 6mm standoffs for ESP32
3. Install M2.5 Nylon screws and standoffs
4. Assemble voltage converter
5. Install battery using velco or zip ties
6. Install ESP32
7. Connect 3.3V cable to power converter
8. Install power switch, tighten well
9. Connect power input to ESP32

<div>

<figure><figcaption></figcaption></figure>

<figure><figcaption></figcaption></figure>

</div>

<div>

<figure><figcaption></figcaption></figure>

<figure><figcaption></figcaption></figure>

<figure><figcaption></figcaption></figure>

</div>

<div>

<figure><figcaption></figcaption></figure>

<figure><figcaption></figcaption></figure>

<figure><figcaption></figcaption></figure>

<figure><figcaption></figcaption></figure>

</div>

<div>

<figure><figcaption></figcaption></figure>

<figure><figcaption></figcaption></figure>

</div>

<div>

<figure><figcaption></figcaption></figure>

<figure><figcaption></figcaption></figure>

</div>

## OLED displays

1. Install OLED displays into the holder
   1. 8x M2.5 6mm screws with 8x nuts
   2. Ensure screen position is correct
      1. Looking from the back
         1. 0x7A is left
         2. 0x78 is righ
2. Install 20mm standoff

<div>

<figure><figcaption></figcaption></figure>

<figure><figcaption></figcaption></figure>

</div>

<div>

<figure><figcaption></figcaption></figure>

<figure><figcaption></figcaption></figure>

</div>

<figure><figcaption></figcaption></figure>

## Top Ring

1. Install RTC on the top ring
   1. 2x 6mm standoffs
   2. 2x M3x6mm screws
2. Install voltage divider 2x6mm screws
3. Connect battery holder to top ring, 2x M3x10mm screws
4. Connect Voltage connector (note orientation)
5. Connect Qwiic connector from RTC to ESP32, 50mm qwiic cable
6. Assemble reed switch inside it's holder. Using square nut and M3x10 screw
7. Install reed switch holder to the top ring 2x M3x10&#x20;
8. Connect OLED qwiic cable to RTC'
9. Install OLED display holder
10. Connect both displays

<div>

<figure><figcaption></figcaption></figure>

<figure><figcaption></figcaption></figure>

</div>

<figure><figcaption></figcaption></figure>

<div>

<figure><figcaption></figcaption></figure>

<figure><figcaption></figcaption></figure>

</div>

<div>

<figure><figcaption></figcaption></figure>

<figure><figcaption></figcaption></figure>

<figure><figcaption></figcaption></figure>

</div>

<div>

<figure><figcaption></figcaption></figure>

<figure><figcaption></figcaption></figure>

<figure><figcaption></figcaption></figure>

</div>

## Assembling rings

1. Install Top ring on bottom ring
   1. Fasten with 3x M3x10 screw from the bottom of the bottom ring
2. Install connector to ADS1115 note the orientation
3. Connect dissolved oxygen cable to the breakout, note orientation
4. Connect turbidity cable to the turbidity breakout board
5. Connect OLED display Qwiic cable to qwiic adapter for RTD

<div>

<figure><figcaption></figcaption></figure>

<figure><figcaption></figcaption></figure>

<figure><figcaption></figcaption></figure>

</div>

<div>

<figure><figcaption></figcaption></figure>

<figure><figcaption></figcaption></figure>

<figure><figcaption></figcaption></figure>

<figure><figcaption></figcaption></figure>

</div>

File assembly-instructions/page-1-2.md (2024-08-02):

# Electronics wiring

## Custom cables

command for generating image from main directory

```
wireviz -f p -o docs/.gitbook/assets/ hardware/analog_harness.yaml
```

<figure><figcaption></figcaption></figure>

## Prepared cables

Cable images from top to down from cable plan

<figure><figcaption></figcaption></figure>

<div>

<figure><figcaption></figcaption></figure>

<figure><figcaption></figcaption></figure>

</div>

<figure><figcaption></figcaption></figure>

## Turbidity voltage divider

<figure><figcaption></figcaption></figure>

Stepping down turbidity output from around 3.5-4.2V to 1.75-2.1V.

Differential negative input is 1.65V. Using ADS1115 gain of 4. Measuring difference between 1.65-2.674V

<figure><figcaption></figcaption></figure>

Pinout is of X9 connector in cable schematic. Extra pins used to daisy chain power wires.

## OLED displays I2C address change

<figure><figcaption></figcaption></figure>

Solder address resistor to the right to change default address of 0x78 to 0x7A. This should be done on the OLED on the right side (left side from the back view like the photo)

## ESP32 3V output to 5V converter

<figure><figcaption></figcaption></figure>

Solder 3V3 and GND pins to the JST female connector. Add hot glue or liquid tape to prevent wires from bending and breaking.&#x20;

## Power switch cable

<figure><figcaption></figcaption></figure>

<figure><figcaption></figcaption></figure>

Cable connecting the battery (female) to the ESP32 (male). GND connects directly, power side goes through toggle switch and reed switch in parallel. \
Reed switch is to be controller via external magnet outside the enclosure, but if for any reason it fails and for debugging additional toggle switch is added that can also turn on the device.

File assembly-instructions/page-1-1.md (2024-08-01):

---
description: Components preparation
---

# Hardware

## 3D printing

Slicing done with PrusaSlicer [https://www.prusa3d.com/page/prusaslicer\_424/](https://www.prusa3d.com/page/prusaslicer\_424/)

### Internal components

<figure><figcaption><p>Orientation</p></figcaption></figure>

1. ConnectingRingTop
2. ConnectingRingBottom
3. VD\_holder
4. BatteryHolder\_v004
5. ReedSwitchHolder

* Material - PETG
* Default settings for
  * 0.2mm speed
  * Generic PETG
* Infill - 100%

<div>

<figure><figcaption></figcaption></figure>

<figure><figcaption></figcaption></figure>

<figure><figcaption></figcaption></figure>

</div>

1. SensorStackAttachment
2. Display\_holder\_1.3

* Material - PETG
* Default settings for
  * 0.2mm speed
  * Generic PETG
* Infill - 100%
* Add smart fill support as shown in images

<figure><figcaption></figcaption></figure>

{% hint style="danger" %}
Cable clamp inner diameter needs to be adjusted to each individual cable size before exporting STL.
{% endhint %}

* Filename: 5x **o-ring-protection** and 10x **CableGland\_cableclamp**
* Material: PETG
* Default settings for 0.2
* Infill - 100%
* Perimeter - 4

### External components

<figure><figcaption><p>Orientation Handle_curved</p></figcaption></figure>

* **Handle\_curved**
  * Filament - PETG
  * Default settings for
    * 0.2mm speed
    * Generic PETG
  * Infill - 100%
  * Add Brim 7mm

<figure><figcaption></figcaption></figure>

* 2x **Clamp\_top** and 2x **Clamp\_bottom**
  * Material: PETG
  * Default settings for
    * 0.2mm speed
  * Infill - 100%

<figure><figcaption></figcaption></figure>

* Filename: knob
* Material: PETG
* Default settings for 0.2
* Infill - 100%
* Perimeter - 4
* Brim (optional)

<figure><figcaption></figcaption></figure>

* Filename: SensorCover
* Material: PETG
* Default settings for 0.2
* Infill - 100%
* Perimeter - 4

<figure><figcaption></figcaption></figure>

* Filename: SensorMountingPlate
* Material: PETG
* Default settings for 0.2
* Infill - 100%
* Perimeter - 4

### Sealing Flanges

<figure><figcaption></figcaption></figure>

{% hint style="danger" %}
Before exporting STL,  measure inside tube diameter and adjust spreadsheet value for flange\_from\_tube to be around 0.6mm smaller than inner diameter. Default inner diameter value is 94mm. flange\_from\_tube value is to compensate from actual tolerances. \
Example, if real inner diamter is 95mm, make flange\_from\_tube to 0.2mm, if real inner diameter is 93mm, make flange from tube -0.8mm.&#x20;
{% endhint %}

* Material: PC blend (natural color)
* Default settings for 0.2 Layer height
  * Perimeter - 6
  * Infill - 100%
  * Brim
    * Width - 20mm
    * Type - Outer and inner brim

### Switch

<figure><figcaption></figcaption></figure>

* Filename: **SwitchSpring** and **SwitchHolder**, **SwitchHolder Mirror**
* Material: PETG
* Default settings for 0.2
* Infill - 100%
* Perimeter - 4

<div>

<figure><figcaption></figcaption></figure>

<figure><figcaption></figcaption></figure>

</div>

* Filename: **SwitchLid\_withText**
* Material: PETG
* Default settings for 0.2
* Infill - 100%
* Perimeter - 4
* Dual color
  * Black external
  * White text and arrows
* Support enforcers
  * On corners
  * Under each letter

<figure><figcaption></figcaption></figure>

* Filename: **Switchslider\_withText**
* Material: PETG
* Default settings for 0.2
* Infill - 100%
* Perimeter - 4
* Dual color
  * White main color
  * Black text ON
  * Black background OFF and inside letter O

##

## Post-processing

### Cleaning up 3D prints

* Debur any parts with brim
* Using a sharp chisel remove any parts required support
* Using a torch lighter remove any stringing if present

### Heat inserts

Parts that require heat inserts

All heatinserts are for M3, insert height is 5.7mm.

* 2xFlangeSeal\_Open
  * 6x top
  * 6x bottom
  * 
* 2xClamp bottom
  * 4x sides, insert from the bottom
  * 2x on 45degree angle, insert from outside
  * 
* 2xClamp top
  * 3x top
  * 2x on 45degree angle, insert from outside
  * 
* Sensor mounting plate
  * 4x sides
  * 
* SwitchHolder and SwitchHolder\_mirror
  * 2x top
  * 

### Coating

## Lids cutting

### Main shape

1.  3D print templates

    1. EndCap\_holePunch
    2. EndCap\_sensorHoles

    
2.  Punch 6 mounting holes

    
3.  Drill mounting holes

    
4.  Add template to mark outline

    
5. Cut outline
6. Debur mounting holes
7. Sand and polish edges

<figure><figcaption></figcaption></figure>

### Sensors and Pressure relief valve modifications

Use the same template for each version

<div>

<figure><figcaption></figcaption></figure>

<figure><figcaption></figcaption></figure>

</div>

* Sensor side&#x20;
  * Punch 5 holes around the center
  * Drill with 16 mm step drill
  * Debur edges
* Pressure relief side
  * Punch 1 center hole
  * Drill with 10mm drill
  * Debur edges

## Tube cutting

1. (Optional) 3D print clamps for guiding the hacksaw
   1. File names-
      1. TubeCuttingClampRoundA
      2. TubeCuttingClampRoundB
      3. TubCuttingHolder
2. Measure 20cm length
3. Add guide clamps
4. Cut
5. Debur inside edges

<table data-card-size="large" data-view="cards"><thead><tr><th></th><th></th><th></th><th data-hidden data-card-cover data-type="files"></th></tr></thead><tbody><tr><td></td><td></td><td></td><td></td></tr><tr><td></td><td></td><td></td><td></td></tr><tr><td></td><td></td><td></td><td></td></tr><tr><td></td><td></td><td></td><td></td></tr><tr><td></td><td></td><td></td><td></td></tr></tbody></table>

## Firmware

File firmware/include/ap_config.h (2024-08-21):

//AquaProber Config
#ifndef AP_CONFIG_H
#define AP_CONFIG_H

// General
#define LOGGING_DELAY       10000 // 1minute
#define SERIAL_BAUD_RATE    115200
#define BATTERY_ALARM_TH    20 //%
#define TIMEZONE_OFFSET     -7200 //In seconds to -2hours
// #define BASELINE_ALTITUDE   384.0
const float BASELINE_ALTITUDE = 384.0;
//Calibration
// #define DO_CALIBRATION      0.583250
const float DO_CALIBRATION = 0.583250;


// #define MS5803_SENSOR
#define MS5837_SENSOR

//Pinout
#define SD_SCK  18
#define SD_MISO 19
#define SD_MOSI 23
#define SD_CS   5 //Thing plus C

#define I2C_SDA 21
#define I2C_SCL 22

#define RGB_LED_PIN     2

#define QWIIC_POWER_PIN 0

//ADS1115 Analog channel selection
#define TURBIDITY_PIN   3
#define DO_PIN          0

//I2C addresses
#define ADDR_MAX17048   0x36
#define ADDR_ADS1115_1  0x48
#define ADDR_EZO_EC     0x64
#define ADDR_EZO_RTD    0x66
#define ADDR_RTC        0x68
#define ADDR_MS5803     0x76
#define ADDR_OLED_LEFT  0x78//0x3C//0x78
#define ADDR_OLED_RIGHT 0x7A//0x3D//0x7A 


//Neopixel
#define COLOR_ORDER GRB
#define CHIPSET     WS2812
#define NUM_LEDS    1
#define BRIGHTNESS  25

//RTD
#define RTD_READ_ATTEMPTS   20

#endif //AP_CONFIG_H

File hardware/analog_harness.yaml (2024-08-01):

connectors:
  X1: &template_HARWIN
    type: HARWIN M20
    subtype: female
    pinlabels: [A+, A3, A2, A1, A0, A-]
    notes: ADS1115 ADC
  X3:
    type: JST-PH
    subtype: female
    pinlabels: [Sensor_out,VCC,GND]
    notes: Turbidity sensor
  X4:
    <<: *template_HARWIN
    pinlabels: [GND, 3.3V, Analog]
    notes: Surveyor DO meter
  X5: &template_qwiic_header
    type: HARWIN M20
    subtype: female
    pinlabels: [GND, 3.3V, SDA,SCL]
    notes: qwiic I2C adapter
  X6:
    <<: *template_HARWIN
    pinlabels: [VCC,N/C,GND,TX,RX]
    notes: RTD Non-isolated EZO
  X7:
    <<: *template_qwiic_header
  X8:
    <<: *template_HARWIN
    pinlabels: [VCC,N/C,GND,TX,RX]
    notes: EC isolated EZO
  X9:
    <<: *template_HARWIN
    pinlabels: [GND,GND,NC,TURB_IN, NC,TURB_OUT, A-, A-, A+, A+,Vref]
    notes: Voltage Divider Board
  F1: &template_ferrule
    style: simple
    type: Crimp ferrule
    subtype: 22AWG
    color: BK
    notes: 5V power converter
  F2:
    <<: *template_ferrule
    color: RD
  Q1: &template_qwiic
    type: QWIIC JST-SHR-04
    subtype: female
    pinlabels: [GND, VCC, SDA, SCL]
    notes: qwiic
    image:
      src: resources/qwiic_cable.png
  Q2:
    <<: *template_qwiic
  Q3:
    <<: *template_qwiic_header
    pinlabels: [GND, 3.3V, SCL, SDA]
    notes: OLED_1
    image:
      src: resources/HARWIN_M20_4.png
  Q4:
    <<: *template_qwiic_header
    pinlabels: [GND, 3.3V, SCL, SDA]
    notes: OLED_2
    image:
      src: resources/HARWIN_M20_4.png
cables:
  W2:
    wirecount: 2
    colors: [RD,BK]
    category: bundle
  W4: &template_i2c
    wirecount: 4
    length: 0.1
    colors: [BK,RD,BU,YE]
  W5:
    <<: *template_i2c
  W_ADS:
    wirecount: 4
    colors: [RD, WH, YE, BK]
    category: bundle
  W_TURB:
    wirecount: 2
    colors: [YE,BK]
    category: bundle
  W_DO:
    wirecount: 3
    colors: [BK,RD,YE]
    category: bundle
  WQ1:
    <<: *template_i2c
  WQ2:
    <<: *template_i2c
    category: bundle
  WQ3:
    <<: *template_i2c

connections:
  -
    - X3: [2]
    - W2: [1]
    - [F2]
  -
    - X9: 1
    - W2: 2
    - [F1]
  -
    - X3: [1,3]
    - W_TURB: [1,2]
    - X9: [4,2]
  -
    - X1: [3,2,1,6]
    - W_ADS: [2,3,1,4]
    - X9: [6,11,9,7]
  -
    - X1: [5]
    - W_DO: [3]
    - X4 : 3
  -
    - X9: [8,10]
    - W_DO: [1,2]
    - X4: [1,2]
  -
    - X5: [GND,3.3V, SDA, SCL]
    - W4: [1-4]
    - X6: [VCC, GND,TX,RX]
  -
    - X7: [GND,3.3V, SDA, SCL]
    - W5: [1-4]
    - X8: [VCC, GND,TX,RX]
  -
    - Q1: [1-4]
    - WQ1: [1-4]
    - Q3: [GND, 3.3V, SDA, SCL]
  -
    - Q4: [GND, 3.3V, SDA, SCL]
    - WQ2: [1-4]
    - Q3: [GND, 3.3V, SDA, SCL]
  -
    - Q4: [GND, 3.3V, SDA, SCL]
    - WQ3: [1-4]
    - Q2: [1-4]

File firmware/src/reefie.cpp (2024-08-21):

#include "reefie.h"


const int Reefie::numLog = 15;
const String Reefie::dataNames[Reefie::numLog] = {
    "unix_timestamp", "human_timestamp", "temperature", "do_volt", "do_saturation", "turb_volt", 
    "turb_ntu", "conductivity", "tds", "salinity", "specific_gravity", 
    "pressure_abs", "depth", "battery_voltage","battery_soc"
};

Reefie::Reefie()
    :   lipo(MAX1704X_MAX17048), // Create a MAX17048
        battery_voltage(0),
        battery_soc(0),
        battery_alert(false),
        #ifdef MS5803_SENSOR
        pressure_sensor(ADDRESS_HIGH),
        #endif
        EC(Ezo_board(ADDR_EZO_EC, "EC")),
        RTD(Ezo_board(ADDR_EZO_RTD, "RTD")),
        state(STATE_INIT),
        readStates(READ_STATE_INIT),
        u8g2_l(U8G2_R0, /* reset=*/ U8X8_PIN_NONE),
        u8g2_r(U8G2_R0, /* reset=*/ U8X8_PIN_NONE)
        
{
  pressure_state.state_current = false;
  fuelgauge_state.state_current = false;
  rtc_state.state_current = false;
  sdCard_state.state_current = false;
  logfile_state.state_current = false;
  ads_state.state_current = false;
  ec_state.state_current = false;
  rtd_state.state_current = false;

  display_cycle = 0;
}

//Public functions
bool Reefie::begin(){
  // Start Serial USB logging
  Serial.begin(SERIAL_BAUD_RATE);
  
  Wire.begin();

  u8g2_r.setI2CAddress(ADDR_OLED_RIGHT); //Right Screen
  u8g2_r.begin();
  u8g2_l.setI2CAddress(ADDR_OLED_LEFT); //Left Screen
  u8g2_l.begin();
  u8g2_l.setFont(u8g2_font_ncenB10_tr);
  u8g2_r.setFont(u8g2_font_ncenB10_tr);
  displayUpdateInit();
  if(initFuelGauge()) fuelgauge_state.state_current = true;
  displayUpdateInit();
  if(initRTC()) rtc_state.state_current = true;
  displayUpdateInit();

  if(initSDCard())
  {
    sdCard_state.state_current = true;
    displayUpdateInit();
    return true;
  }else return false;
    
}

void Reefie::deepSleepStart(){
    Serial.println("ESP32 is going into deep sleep now, and will not wake up until manually power cycled.");
    // Ensure no wake-up source is set
    esp_sleep_disable_wakeup_source(ESP_SLEEP_WAKEUP_ALL);
    // Delay to allow serial message to be sent
    delay(2000);
    // Enter deep sleep
    esp_deep_sleep_start();
}

//Private functions
bool Reefie::initSDCard(){
  if (!SD.begin(SD_CS)) {
    Serial.println("Card Mount Failed");
    return false;
  }
  Serial.println("SD Card initialized.");
  return true;
}

bool Reefie::initRTC(){
    if (!rtc.begin(&Wire)) {
    Serial.println("Couldn't find RTC");
    return false;
    }else{
      if (rtc.lostPower()){
          // Get compile time
          DateTime compileTime(F(__DATE__), F(__TIME__));
          // Subtract 2 hours (7200 seconds) to adjust to UTC 0 timezone
          DateTime adjustedTime = compileTime + TimeSpan(TIMEZONE_OFFSET);
          // Adjust the RTC time
          rtc.adjust(adjustedTime);
          Serial.println("RTC power lost, reinitialzied time");
      }
      return true;
    }
}

bool Reefie::initFuelGauge(){
  if (lipo.begin(Wire) == false){ // Connect to the MAX17043 using the default wire port
      Serial.println(F("MAX17043 not detected"));
      // deepSleepStart();
      return false;
  }else
  {
    // Quick start restarts the MAX17043 in hopes of getting a more accurate
    // guess for the SOC.
    lipo.quickStart();

    return true;
  }
}

void Reefie::setupLogFile(){
    createBaseDirectory();
    fileName = generateFileName();
    createNewFile(fileName);
    writeHeader(fileName);
    logfile_state.state_current = true;
}

bool Reefie::checkPressureSensor(TwoWire &wirePort) {
  #ifdef MS5803_SENSOR
    // Begin communication with the sensor
    pressure_sensor.begin(Wire, 0x76); // Or, from v1.1.3, we can also do this

    // Attempt to read a coefficient from the sensor's PROM
    wirePort.beginTransmission(0x76);
    wirePort.write(CMD_PROM);
    if (wirePort.endTransmission() != 0) {
        return false;
    }
    #endif
    #ifdef MS5837_SENSOR
    if(!pressure_sensor.init()) return false; 
    #endif

    return true;
}

void Reefie::setupSensors(){

  // Begin communication with the sensor
    if(checkPressureSensor(Wire))
    {
      #ifdef MS5803_SENSOR
      // pressure_sensor.begin(Wire, 0x76); // Or, from v1.1.3, we can also do this
      pressure_sensor.reset();
      pressure_baseline = pressure_sensor.getPressure(ADC_4096);
      #endif

      #ifdef MS5837_SENSOR
      pressure_sensor.setModel(MS5837::MS5837_30BA);
      pressure_sensor.setFluidDensity(997); // kg/m^3 (997 for freshwater, 1029 for seawater)
      #endif

      pressure_state.state_current = true;
    }
    
      displayUpdateInit();

      if (!ads.begin(ADDR_ADS1115_1, &Wire)) {
      Serial.println("Failed to initialize ADS.");
    }else{
      ads_state.state_current = true;
    }
    displayUpdateInit();

    Serial.println("Configuring Conductivity sensor");
    EC.send_cmd("k,1.0");        //send command to Set probe type
    delay(300);
    EC.send_cmd("o,ec,1");        //send command to enable EC output
    delay(300);
    EC.send_cmd("o,tds,1");        //send command to enable TDS output
    delay(300);
    EC.send_cmd("o,s,1");        //send command to enable salinity output
    delay(300);
    EC.send_cmd("o,sg,1");      //send command to enable specific gravity output
    delay(300);

    char receive_buffer[32];                  //buffer used to hold each boards response
    

    Serial.print("Testing EC - ");
    EC.send_read_cmd();
    delay(1000);
    EC.receive_cmd(receive_buffer, 32);   //put the response into the buffer
    delay(300);
    if(EC.get_error() == Ezo_board::SUCCESS) ec_state.state_current = true;
    Serial.println(EC.get_error());
    displayUpdateInit();

    Serial.print("Testing RTD - ");
    if(RTDreadLoop()) rtd_state.state_current = true;
    Serial.println(RTD_temp);
    displayUpdateInit();
    
}

bool Reefie::RTDreadLoop(){
  read_attempts = 0;
  bool result = true;
    do{
      RTD.send_read_cmd();
      delay(600);
      RTD.receive_read_cmd();
      read_attempts++;
    }while(RTD.get_error() != Ezo_board::SUCCESS && read_attempts!=RTD_READ_ATTEMPTS);
    if(read_attempts == RTD_READ_ATTEMPTS) result = false;
    RTD_temp = RTD.get_last_received_reading();
    return result;
}

void Reefie::createBaseDirectory(){
  if (!SD.exists("/data")) {
    if (!SD.mkdir("/data")) {
      Serial.println("Failed to create base directory: /data");
      return;
    }else{
      Serial.println("Created base directory: /data");
    }
  }else{
    Serial.println("Base directory exists: /data");
  }
}

String Reefie::generateFileName() {
  String name;
  DateTime time_now = rtc.now();
  char folderName[11];
  char fileName[23];
  int fileIndex = 0;

  while (true) {
    snprintf(folderName, sizeof(folderName), "%04d-%02d-%02d",
          time_now.year(), time_now.month(), time_now.day());
    snprintf(fileName, sizeof(fileName), "%04d-%02d-%02d_%02d-%02d_%03d",
          time_now.year(), time_now.month(), time_now.day(),
          time_now.hour(), time_now.minute(), fileIndex);
    name = "/data/" + String(folderName) + "/" + String(fileName) + ".csv";

    if (!SD.exists(name)) {
      break;
    }
    fileIndex++;
  }
  return name;
}

void Reefie::createNewFile(const String &name) {
  // Extract the directory path
  int lastSlashIndex = name.lastIndexOf('/');
  String dirPath = name.substring(0, lastSlashIndex);

  // Check if the directory exists and create it if it doesn't
  if (!SD.exists(dirPath)) {
    if (!SD.mkdir(dirPath)) {
      Serial.println("Failed to create directory: " + dirPath);
      return;
    }else{
      Serial.println("Created directory: " + dirPath);
    }
  } else{
    Serial.println("Directory exists: " + dirPath);
  }

  dataFile = SD.open(name, FILE_WRITE);
  if (!dataFile) {
    Serial.println("Failed to create file: " + name);
    return;
  }
  dataFile.flush();
  dataFile.close();
  Serial.println("Created file: " + name);
}

void Reefie::readConfigFile(){
  const char* configFileName = "/config.txt";
  File configFile;
  if (SD.exists(configFileName)) {
    configFile = SD.open(configFileName, FILE_READ);
    if (configFile) {
      String line;
      while (configFile.available()) {
        line = configFile.readStringUntil('\n');
        parseConfigLine(line);
      }
      configFile.close();
    } else {
      Serial.println("Failed to open config file for reading");
    }
  } else {
    Serial.println("Config file does not exist. Creating with default values.");
    createDefaultConfigFile(configFileName);
  }

}

void Reefie::parseConfigLine(String line) {
  line.trim();
  int delimiterIndex = line.indexOf('=');
  if (delimiterIndex > 0) {
    String key = line.substring(0, delimiterIndex);
    String value = line.substring(delimiterIndex + 1);
    key.trim();
    value.trim();

    if (key == "LOGGING_DELAY") {
      logging_delay_config = value.toInt();
    } else if (key == "BATTERY_ALARM_TH") {
      battery_alarm_th_config = value.toInt();
    } else if (key == "BASELINE_ALTITUDE") {
      baseline_altitude_config = value.toFloat();
    } else if (key == "DO_CALIBRATION") {
      do_calibration_config = value.toFloat();
    }
    Serial.println(key + " = " + value);
  }
}

void Reefie::createDefaultConfigFile(const char* configFileName) {
  File configFile = SD.open(configFileName, FILE_WRITE);
  if (configFile) {
    configFile.printf("LOGGING_DELAY=%d\n", LOGGING_DELAY);
    configFile.printf("BATTERY_ALARM_TH=%d\n", BATTERY_ALARM_TH);
    configFile.printf("BASELINE_ALTITUDE=%f\n", BASELINE_ALTITUDE);
    configFile.printf("DO_CALIBRATION=%.6f\n", DO_CALIBRATION);
    configFile.close();
    Serial.println("Default config file created.");
    logging_delay_config = LOGGING_DELAY;
    battery_alarm_th_config = BATTERY_ALARM_TH;
    baseline_altitude_config = BASELINE_ALTITUDE;
    do_calibration_config = DO_CALIBRATION;
  } else {
    Serial.println("Failed to create config file");
  }
}

void Reefie::writeHeader(const String &name)
{
  dataFile = SD.open(name, FILE_APPEND);
  if (dataFile) {
    for (int i = 0; i < numLog; i++) {
      dataFile.print(dataNames[i]);
      if (i < numLog - 1) {
        dataFile.print(",");
      }
    }

    dataFile.println(); // Example value to append
    dataFile.close();
    Serial.println("Data written to file: " + name);
  } else {

    Serial.println("Failed to open file for appending");

  } 
}

void Reefie::parseEZOData()
{
  EC_str = strtok(EC_data, ",");       //let's parse the string at each comma.
  TDS = strtok(NULL, ",");                  //let's parse the string at each comma.
  SAL = strtok(NULL, ",");                  //let's parse the string at each comma 
  SG = strtok(NULL, ",");                  //let's parse the string at each comma.

  EC_float=atof(EC_str);
  TDS_float=atof(TDS);
  SAL_float=atof(SAL);
  SG_float=atof(SG);
}
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

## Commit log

2024-05-29 GITBOOK-8: Added pressure sensor info
2024-05-29 GITBOOK-9: DFRobot sensors info
2024-05-30 GITBOOK-16: Added ph sensor and EZO board addresses
2024-05-30 custom cable init
2024-05-30 GITBOOK-20: command for generating wireviz
2024-06-04 added ezo boards
2024-06-06 added pressure sensor
2024-06-26 GITBOOK-1: 3D printing setup
2024-07-11 GITBOOK-10: Added some print settings
2024-07-11 GITBOOK-11: Tube cutting
2024-07-17 OLED wire harness
2024-07-25 Updated wiring and OLED
2024-07-30 GITBOOK-16: pressure sensor docs
2024-07-30 GITBOOK-18: other pressure done
2024-07-31 GITBOOK-21: splitting sensors out
2024-08-01 GITBOOK-23: 3D printing docs
2024-08-01 GITBOOK-24: switch printing
2024-08-01 GITBOOK-27: Heat inserts
2024-08-02 3D files added
    [Master-BatteryHolder_v004 (Meshed).stl, Master-CableGland_cableclamp (Meshed).stl, Master-Clamp_bottom003.stl, Master-Clamp_top (Meshed).stl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]
2024-08-02 GITBOOK-30: voltage divider
2024-08-02 GITBOOK-31: Cables, power switch
2024-08-02 GITBOOK-32: Sensor stack
2024-08-05 GITBOOK-37: battery holder
2024-08-05 GITBOOK-39: Sensor holder
2024-08-08 GITBOOK-40: install cable glands
2024-08-21 added MS5837 sensor
